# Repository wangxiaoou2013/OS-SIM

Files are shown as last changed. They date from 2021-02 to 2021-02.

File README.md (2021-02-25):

# OS-SIM
Configuration and detailed explanation of Othogonally Scanning Structured Illumination Microscopy (OS-SIM).

## Introduction
OS-SIM (Orthogonally Scanning-Structured Illumination Microscopy) is a light-sheet based SIM which can enhance the resolution of sample on two orthogonal axis. It is designed and set up for the physics experiment course, and now generate the sinusoidal pattern in two direction on cleared brain slice successfully. Reconstruction and result is developing and analyzing now.

## Configuration
### Detailed layout
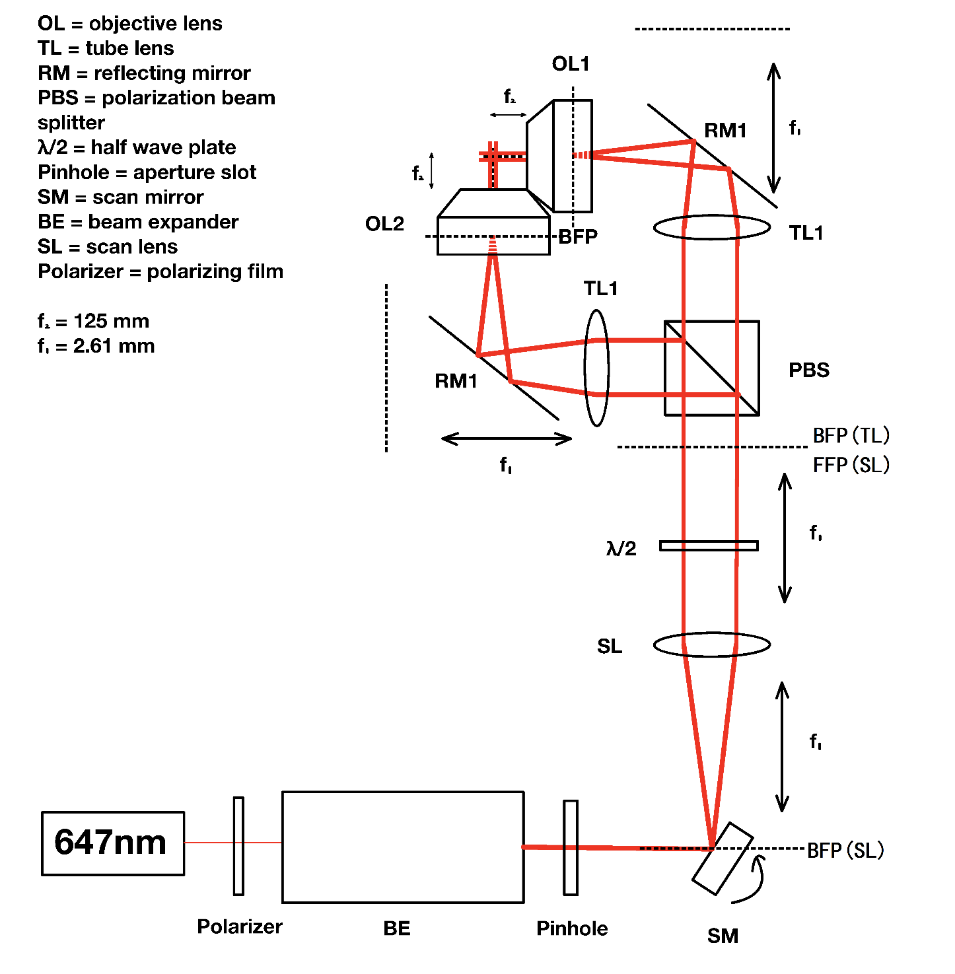
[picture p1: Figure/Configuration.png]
Full configuration of OS-SIM

The basic configuration followed this figure. We use a modulated laser with a sinusoidal oscillation on time and a Galvo mirror together to generate the light sheet with patter, and then use two 4f-system to transfer the virtual fan-shaped light source to the BFP of objective lens, then generate structured light sheet illumination on the focal plane of two objective lens, whose focal points coincide. In order to generate the pattern on two direction alternately, we use a polarization separating system with a polarizer, half wave plate and PBS to realize that easily. When we want to switch the direction, the only thing we need to do is to rotate the half wave plate until the pattern we want appear in the microscope. Beam splitter is used to make the light plot on BFP big enough and then get a thinger and clearer pattern.
### Material List
| Material | Number in figure | Model | Quantity | Comments |
|  ----  | ----  |  ----  | ----  | ----  |
| Laser |	647nm | Laser	OBIS LX/LS 647nm | 1 | 647nm |
| Polarizer | Polarizer |	BEIJING DH TECH |	1	| |
| Half wave plate |	λ/2 |	BEIJING DH TECH	| 1 | |
| Aperture | Pinhole | Thorlabs ID25/M | 1 | Ø25.0 mm |
| Beam extender lens | BE |	Thorlabs BE05-10-A | 1 | 5-10X |
| Galvo mirror | SM |	Thorlabs GVS212/M |	1	|
| Lens | SL, TL1, TL2 |	AC254-125-A |	3 |	f=125mm |
| Polarization Beam Splitter | PBS | LBTEK MPBS641 | 1 | |
| Reflector | RM1, RM2 | PF1011-F01	| 2	| |
| Objective lens for imaging |	OL1, OL2 | OLYMPUS UMPLFLN20XW | 1 |	WD=3.5mm | 20X NA=0.5 |
| Objective lens for illumination | OL3 | Mitutoyo NIR | 2 | f=20mm 20x NA=0.4 |
| CMOS camera|	|	PCO panda |	1	| |
| NI controller card | | NI USB-6008 | 1 | |
| Signal generator | | SIGLENT SDG1032X |	1	| |
| Adjustment bracket for objective lens |	| OLYMPUS |	1 |	f=180mm |
| Camera adapter | | OLYMPUS U-TV0.5XC3 |	1	| |
### Chamber
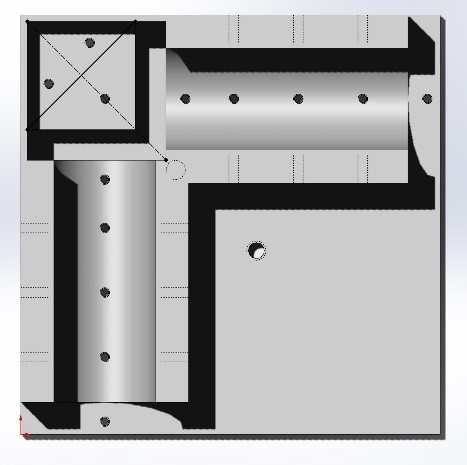
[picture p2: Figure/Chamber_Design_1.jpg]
Chamber1

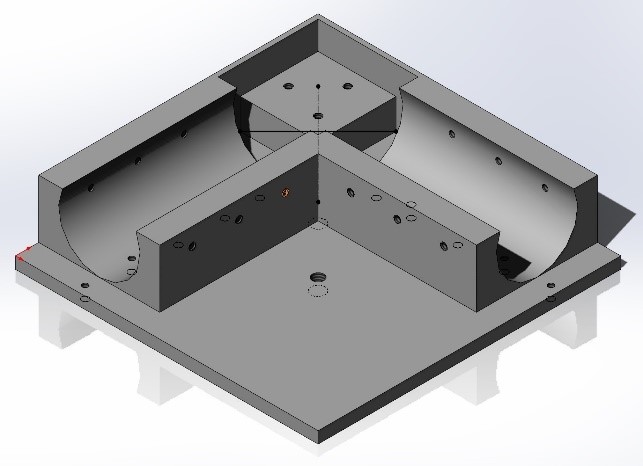
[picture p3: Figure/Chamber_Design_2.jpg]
Chamber2


We designed a chamber for the microscope, which is compatible with refractive index matching and tiny adjustment for objective lens and sample. It should be redesigned when you choose different lens.

## Blueprint
The blueprints for whole system and chamber are available [here](https://github.com/wangxiaoou2013/OS-SIM/tree/master/Blueprint).

## Real Equipment
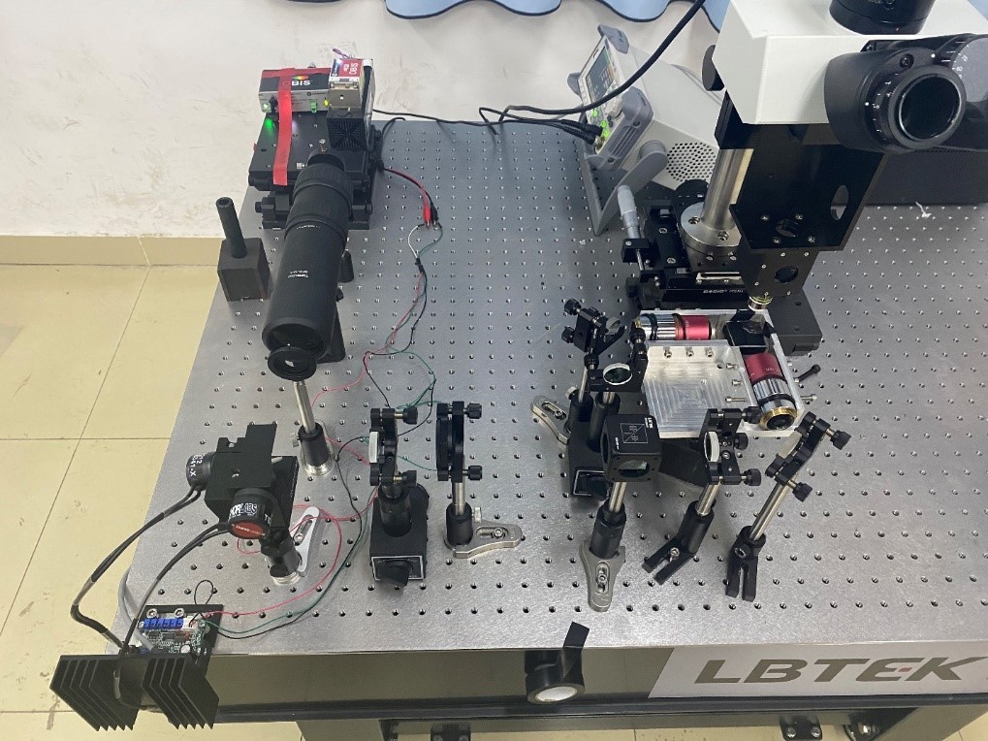
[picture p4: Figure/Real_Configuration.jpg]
Real configuration


## Result of pattern
We recorded the pattern in fluorescence dye:

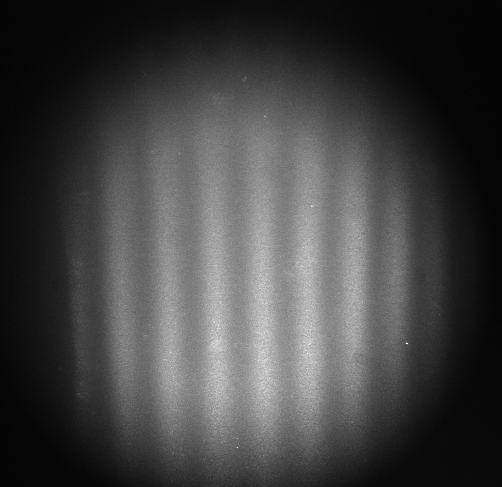
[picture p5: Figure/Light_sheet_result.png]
Light sheet


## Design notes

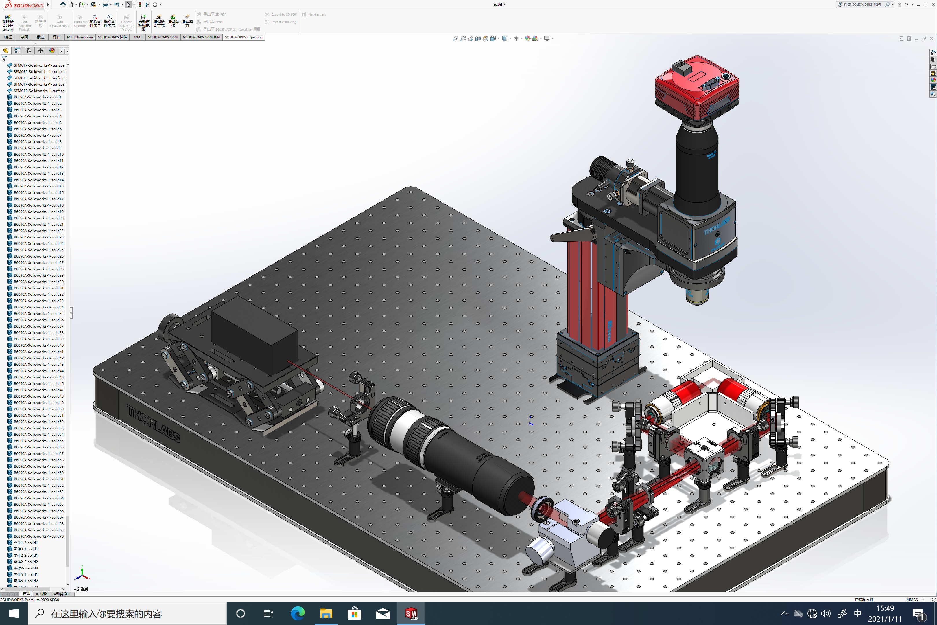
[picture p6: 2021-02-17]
Figure/Solidworks_Design.png

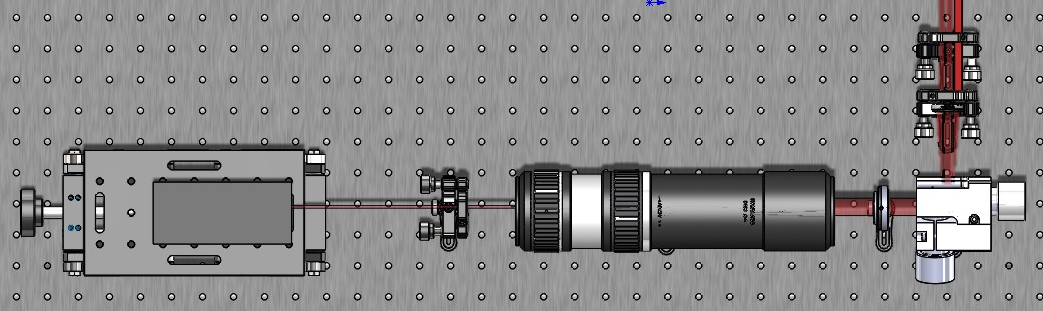
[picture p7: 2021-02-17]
Figure/Light_Sheet_Generation_System.png

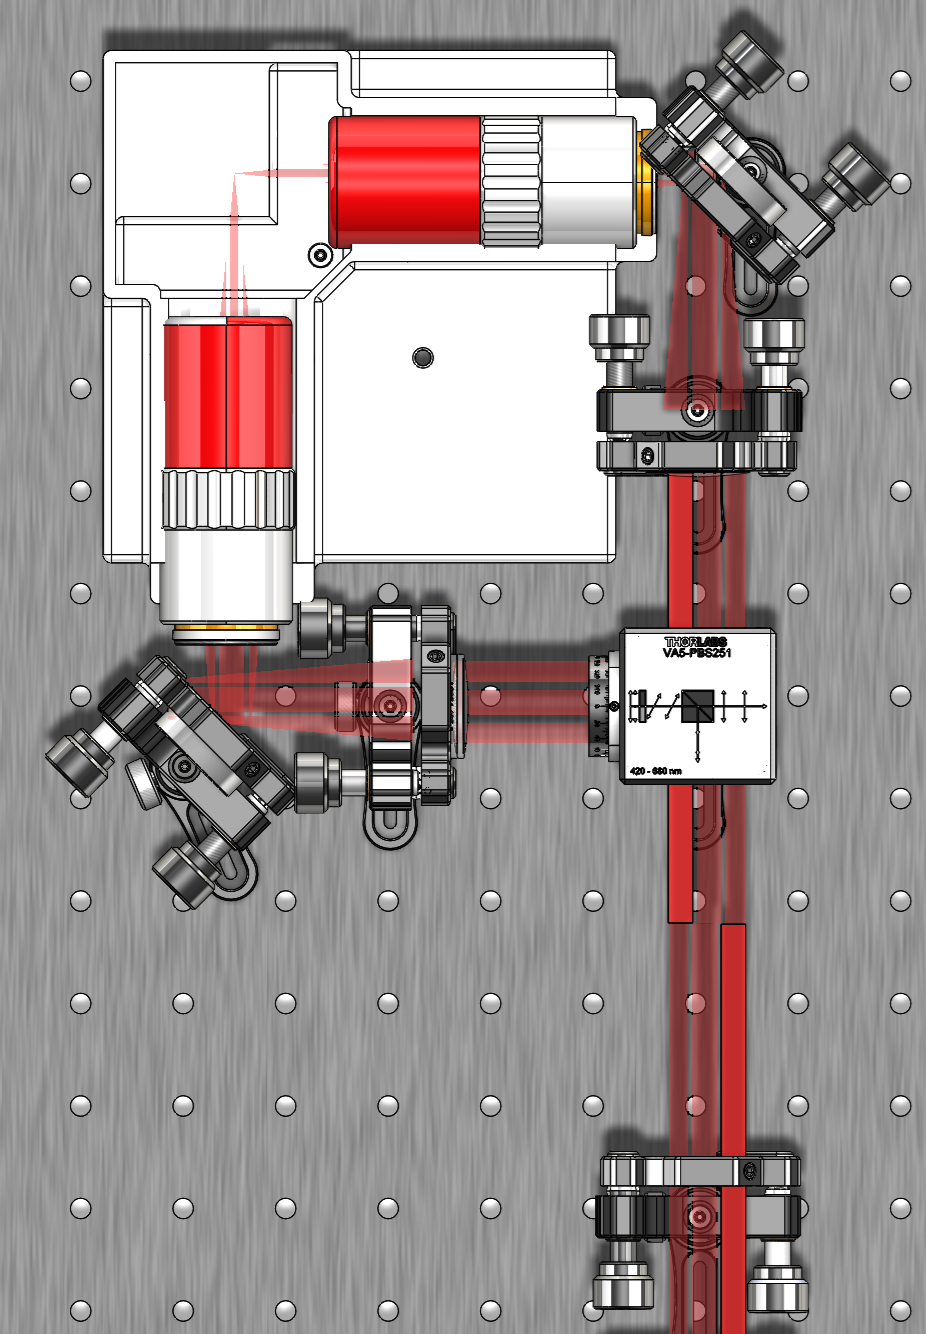
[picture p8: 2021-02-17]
Figure/Seperating_System.png

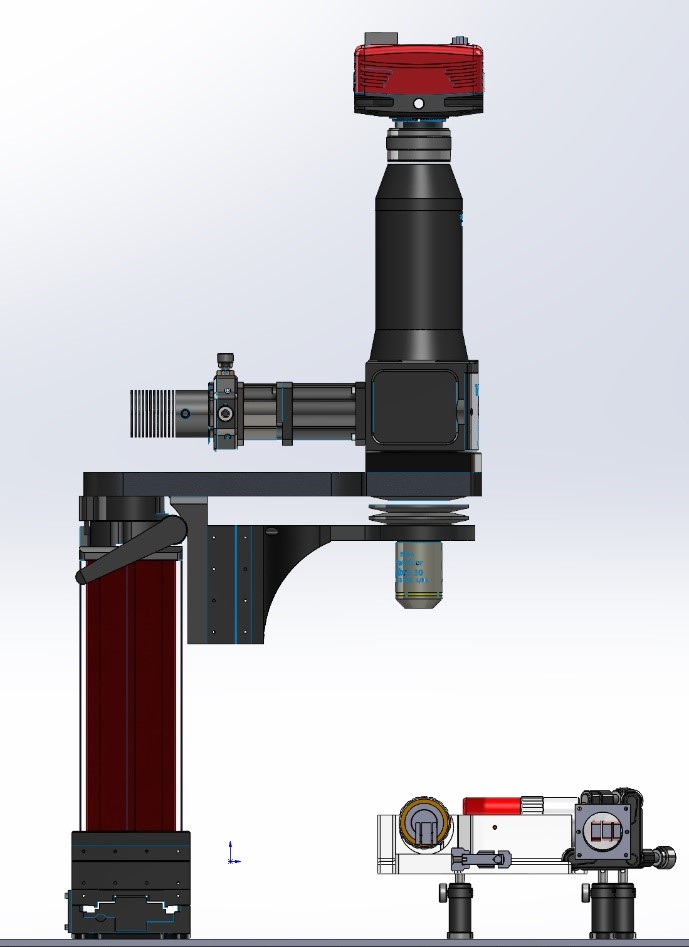
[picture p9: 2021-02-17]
Figure/Imaging_System.jpg

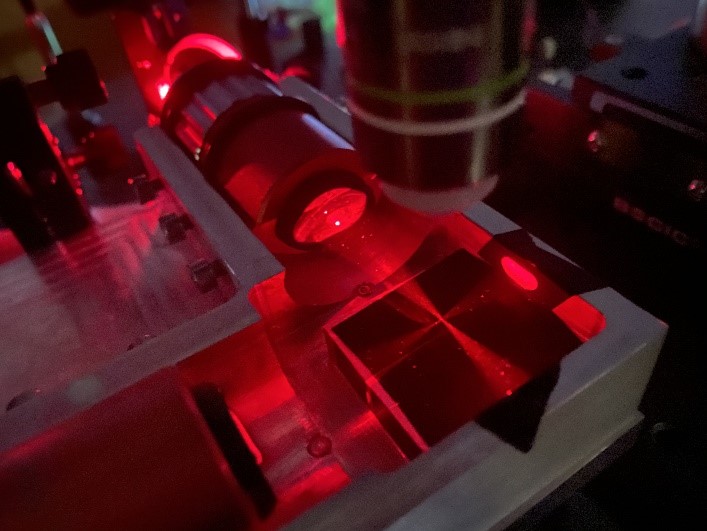
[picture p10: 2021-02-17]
Figure/Real_Chamber.jpg

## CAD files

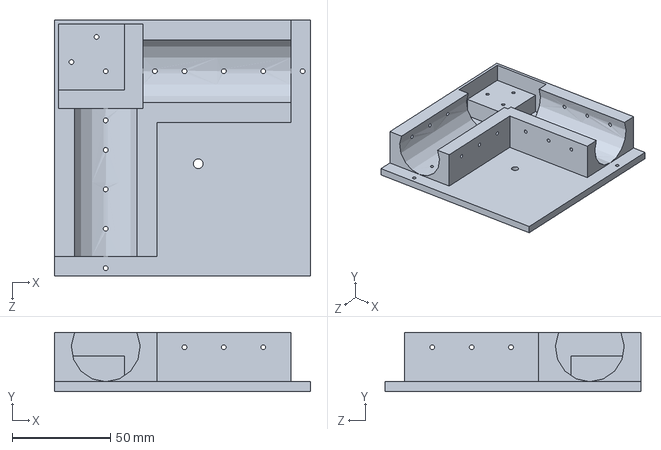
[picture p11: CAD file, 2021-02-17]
Blueprint/Chamber.SLDPRT
130.0 x 30.0 x 130.0 mm
